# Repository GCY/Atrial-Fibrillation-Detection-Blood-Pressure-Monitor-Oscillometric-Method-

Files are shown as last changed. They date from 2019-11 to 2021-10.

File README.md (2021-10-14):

# Atrial-Fibrillation-Detection-Blood-Pressure-Monitor-Oscillometric-Method-
This project is electronic blood pressure monitor research platform with Oscillometric method, include SBP and DBP estimate algorithm, Atrial Fibrillation detection algorithm, calibration curve, GUI tool for fine-tune BP algorithm...etc, ofcourse, this is research use only.

<p align="center">
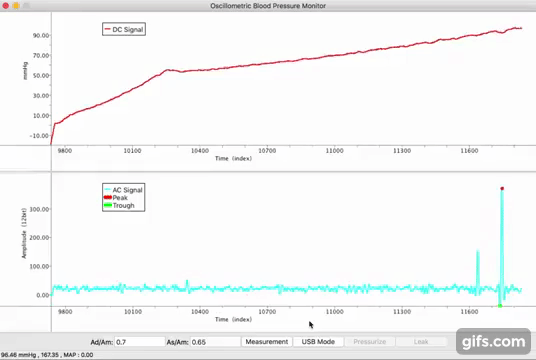
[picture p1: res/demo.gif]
  
</p>  

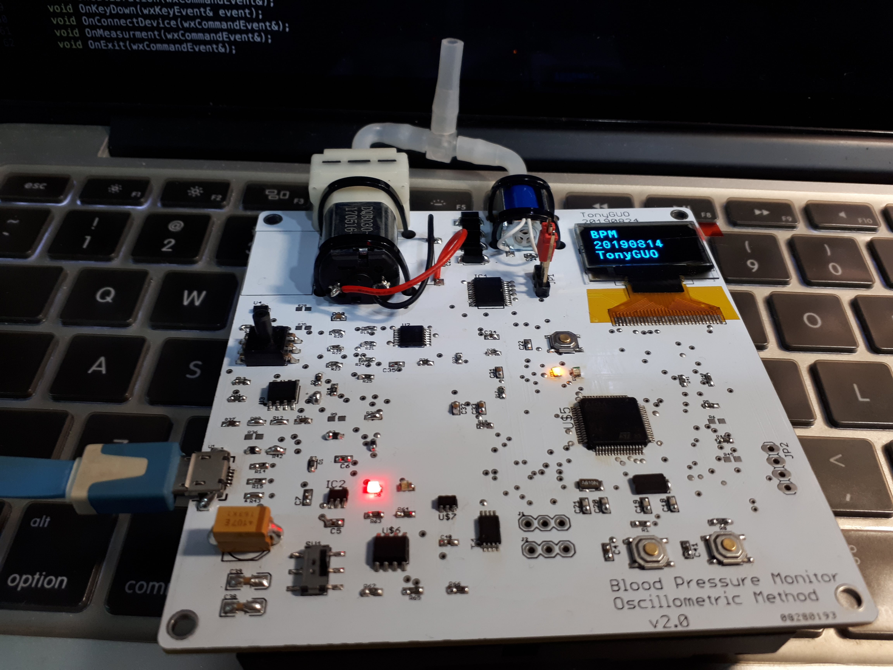
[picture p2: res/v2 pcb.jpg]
  

## Blood Pressure Measurement Oscillometric Method

The oscillometric method was first demonstrated in 1876 and involves the observation of oscillations in the sphygmomanometer cuff pressure which are caused by the oscillations of blood flow, It uses a sphygmomanometer cuff, like the auscultatory method, but with an electronic pressure sensor (transducer) to observe cuff pressure oscillations, electronics to automatically interpret them, and automatic inflation and deflation of the cuff. The pressure sensor should be calibrated periodically to maintain accuracy.

A new analysis of relevant anatomy, physiology and physics reveals the mechanisms underlying the production of cuff pressure oscillations as well as a way to extract systolic and diastolic pressures from the envelope of oscillations in any individual subject. Stiffness characteristics of the compressed artery segment can be extracted from the envelope shape to create an individualized mathematical model. The model is tested with a matrix of possible systolic and diastolic pressure values, and the minimum least squares difference between observed and predicted envelope functions indicates the best fit choices of systolic and diastolic pressure within the test matrix.

In practice the different methods do not give identical results; an algorithm and experimentally obtained coefficients are used to adjust the oscillometric results to give readings which match the auscultatory results as well as possible. Accurate extraction of systolic and diastolic pressures from the envelope of cuff pressure oscillations remains an open problem in biomedical engineering. Since many oscillometric devices have not been validated, caution must be given as most are not suitable in clinical and acute care settings.

via [wiki.](https://en.wikipedia.org/wiki/Blood_pressure_measurement)

## Features
- [x] Blood Pressure Measurment - Systolic, Diastolic, Mean
- [x] Atrial Fibrillation Detection - Irregular Pulse Peak , Irregular Heart Beats
- [x] GUI Toos - Algorithm Finetune
- [x] ADC Clibration to Mercury Manometer Pressure - Polynomial Curve Fit
- [x] RAW Data Record

## Hardware

Project create is Eagle PCB 8.1.0 .</br>

<strong>V2 version, D1(BAT20) should be replaced with zero ohm resistor.</strong></br>

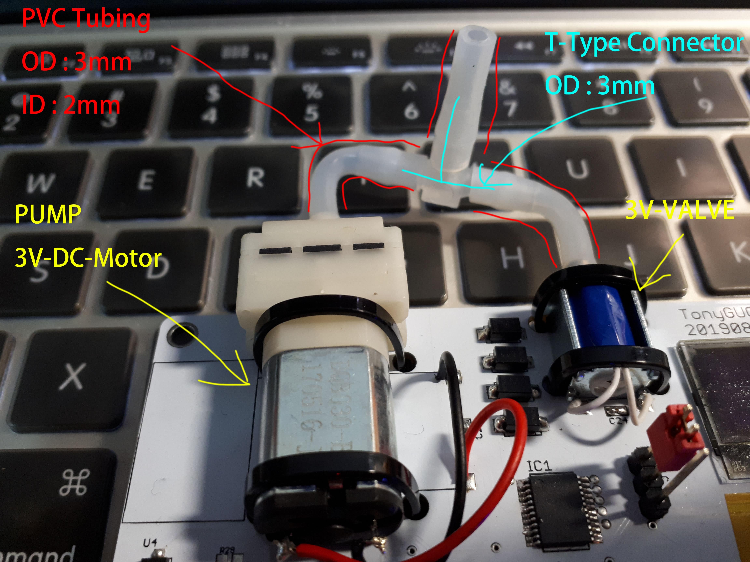
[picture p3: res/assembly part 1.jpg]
 

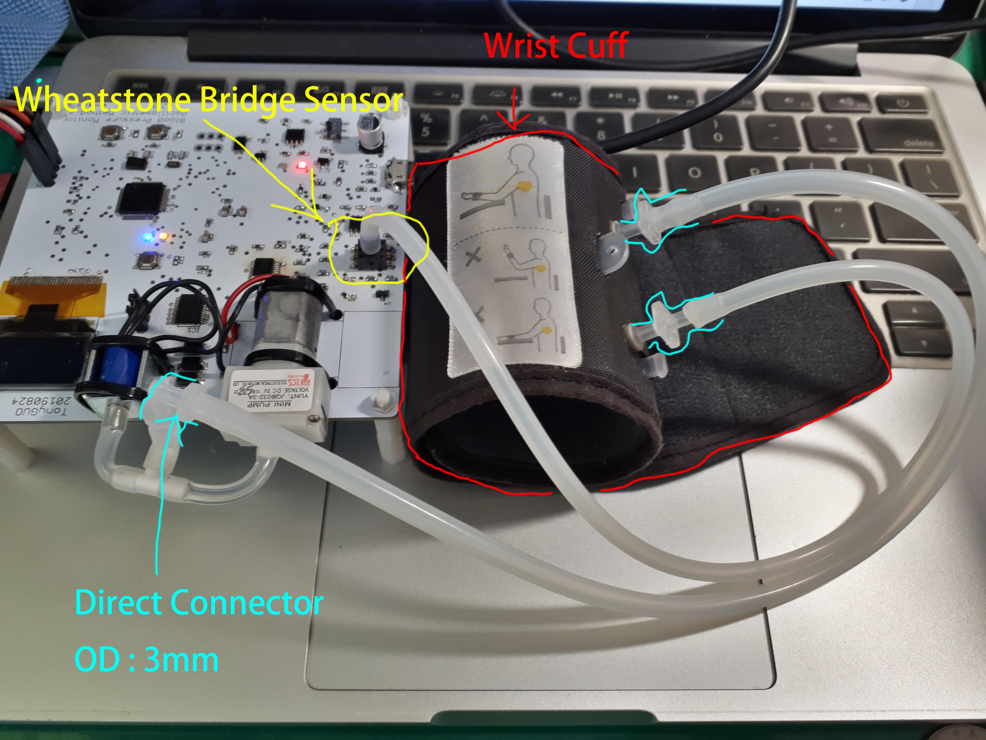
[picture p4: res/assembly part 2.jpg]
 

 

### Key Component List

- Electronics
  - TB6612FNG (for PUMP and VALVE PID control)
  - MPS-3117-006GC A2/A3(MEMS Wheatstone Bridge)
- Mechatronic
  - 3V DC Air Pump Motor(JQB032-3A or DQB030-A-3V)
  - 3V DC Electric Solenoid Valve(JQF1-3C1/DC3V Mini 10mm*15mm)
- Cuff and Tubing
  - 2mm*4mm Silicone Rubber Tubing x 2(20cm~30cm, for wrist cuff input and output)
  - 2mm*4mm Silicone Rubber Tubing x 3(5cm~10cm, for T Type connector)
  - 2mm*3mm T Type Plastic Barbed Connector
  - 2mm*3mm Straight Plastic Barbed Connector x 3
  - Wrist Air Cuff Input/Output(2 pinhole 2mm~3mm)
  
### Configure for Motor Electric Drives With Independent Power Supply - Battery2(U$19)
- J1, J2 pin1 connect to pin2 - battery2 charge
- J1, J2 pin2 connect to pin3 - motor drive with independent power supply
- JP1 pin1 connect to pin2 - motor drive with VCC
- JP1 pin2 connect to pin3 - motor drive with independent power supply

## Firmware

### Build and Burn The .elf
- 1.cd src/BPM
- 2.make
- 3.load main.elf

### Key Parameters

PWM_Freq is DC Motor PWM frequency.</br>
TIM_Prescaler = (168M/2)/1M = 84M</br>
TIM_Period = TIMER_PWM_MAX/PWM_Freq = 1000</br>

TIM = 84M / TIM_Prescaler = 1M</br>
TIM = 1M / TIM_ClockDivision = 1M</br>
1M / (TIM_Period + 1) = 1000Hz (1ms)</br>
<pre><code>
const uint16_t PWM_Freq = 1000;
</code></pre>

ARR = TIMER_PWM_MAX;</br>
CCR = 0 to TIMER_PWM_MAX = 0 to 100% PWM.</br>
In this case, PID PWM step 1 to 100 mapped to 100000 to 1000000.</br>
TIMER_PWM_33 and TIMER_PWM_40 is 33% and 40% PWM for calibration hand control.</br>
<pre><code>
const uint32_t PID_PWM_MIN = 1;
const uint32_t PID_PWM_MAX = 100;
const uint32_t TIMER_PWM_MIN = 100000;
const uint32_t TIMER_PWM_MAX; = 1000000;
const uint32_t TIMER_PWM_33 = 330000;
const uint32_t TIMER_PWM_40 = 400000;
</code></pre>

This is PID parameter, you need to redefine in ResetMeasurementParameter() function.</br>
<pre><code>
Kp = 2, Ki = 0.3, Kd = 0.001; // for JQB032-3A
</code></pre>

AC signal amplitude point of Systolic and Diastolic BP.</br>
<pre><code>
float as_am_value = 0.65f;
float ad_am_value = 0.7f;
</code></pre>

Polynomial curve fitting is generated from 『Calibration ADC-DC to Mercury Manometer Pressure』, you'll need to create 『curve.csv』and execute PC-GUI software main.app or BPM.exe in the same folder, it will output the『equation.txt』.</br>
e.g. degree = 2, equation.txt format is : (-1.0620516546)x^0+(0.1262915457)x^1+(-0.0000012119)x^2 </br>
<pre><code>
float a[3] = {-0.0000012119f,0.1262915457f,-1.0620516546f};
</code></pre>

If pulse_value_N / total_pulse_value_mean > IPP_Ratio, pulse_N is irregular pulse peak, and IPP ratio range 15%~25%.</br>
If IPP number / total_pulse_number > IHB_Ratio, this measurement is irregular heart beat.</br>
If two or more IHB of the three BP measurements, AF detected.<br>
<pre><code>
const float IPP_Ratio = 0.2f;
const float IHB_Ratio = 0.2f;
</code></pre>

### Operation Flowchart
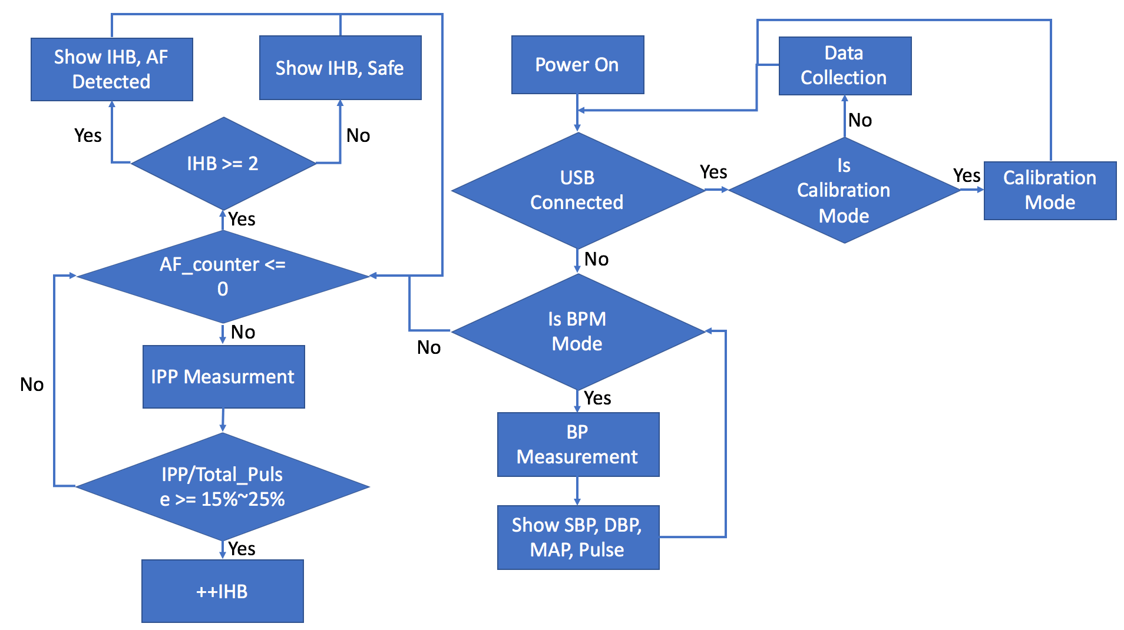
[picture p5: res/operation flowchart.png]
  

### DC/AC Signal Process Flowchart
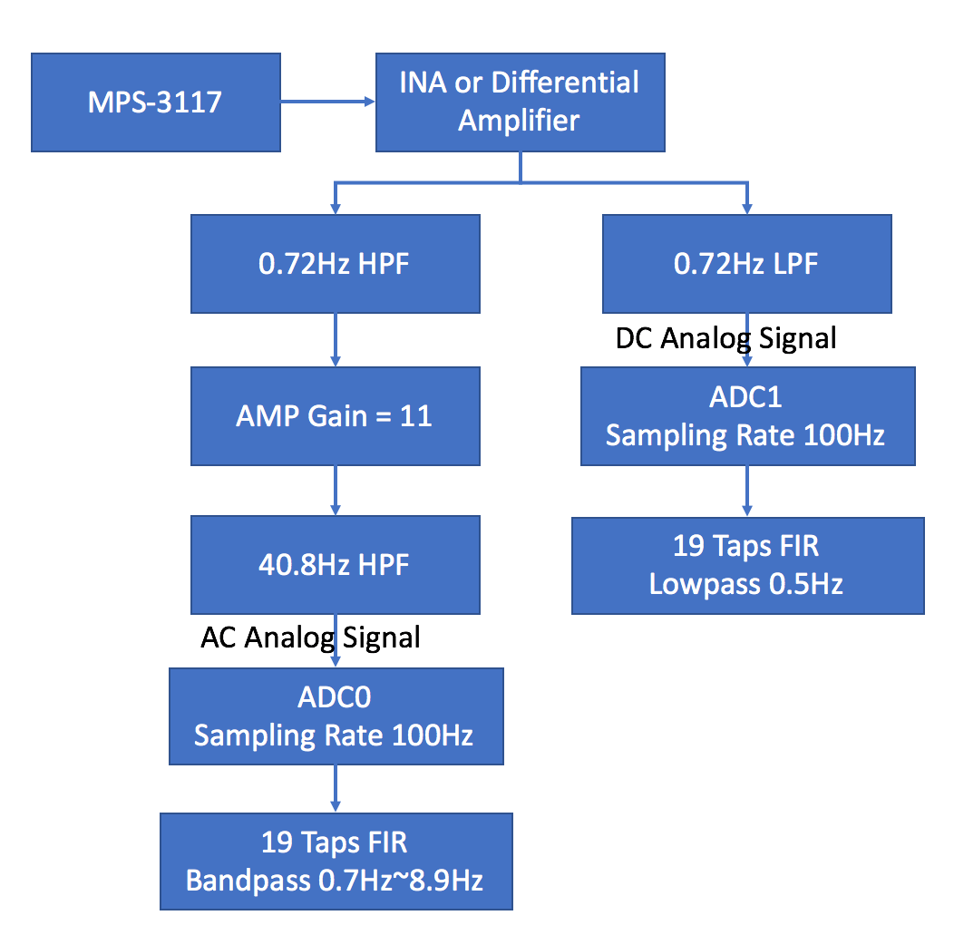
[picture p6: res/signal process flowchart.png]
  

### Measurment Flowchart
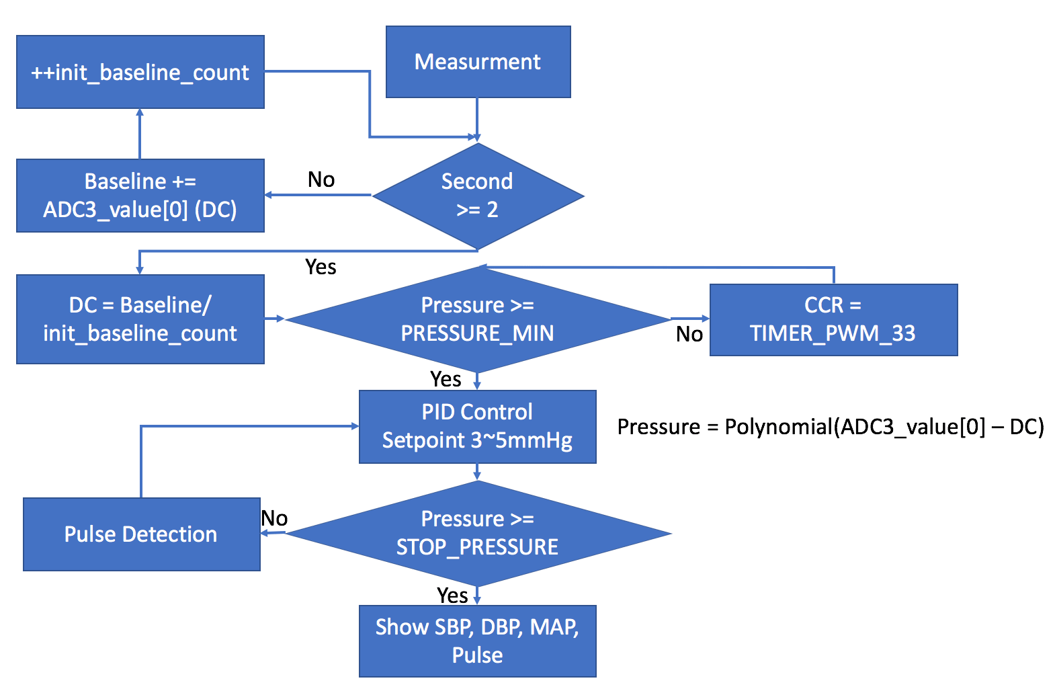
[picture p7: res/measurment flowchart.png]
 

### BPM Mode Demo
Audi R8 (https://youtu.be/4AQXaJOquz4)

## Software

### AFib-BPM GUI Demo
Audi R8 (https://youtu.be/8z78SInvyog)

### Build
- Win10
  - 1.Open BPM.sln
  - 2.Rebuild
- Mac High Sierra
  - 1.make
  
### Dependence
- Win10
  - wxWidgets 3.1.2
  - VS2017 - MSVC 10.0.17763-SDK
- Mac High Sierra
  - wxWidgets 3.x
  - g++

### Parameters Setup
When burning the firmware for the first time, you must set the PID control and blood pressure algorithm parameters. After the PC-Host and VCP are successfully connected, select the Tuning menu to adjust the parameters.</br>

  
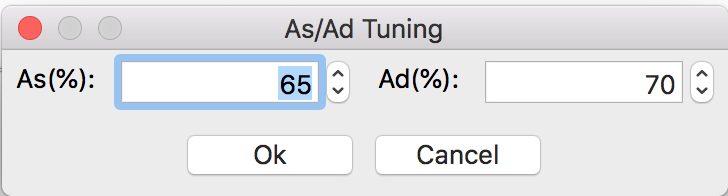
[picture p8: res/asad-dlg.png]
  

Display the parameters that have been set. If the parameters are unset, the value is "0xFFFFFFFF" in sector11 of flash. The PID parameters shown in the figure need to be divided by hundred. (for example, P = 290, in firmware, P is 2.9 .)</br>

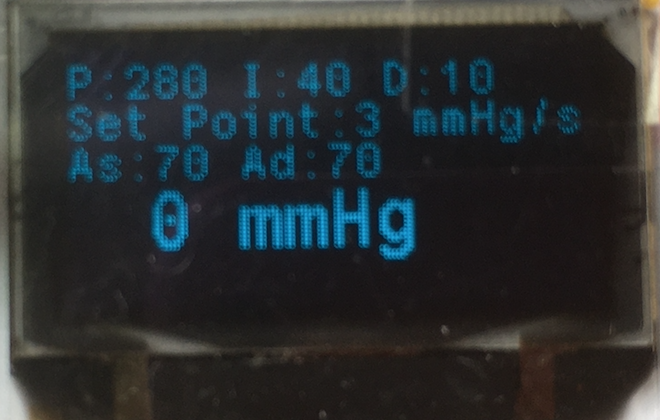
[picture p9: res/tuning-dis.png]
  

### Mac High Sierra GUI
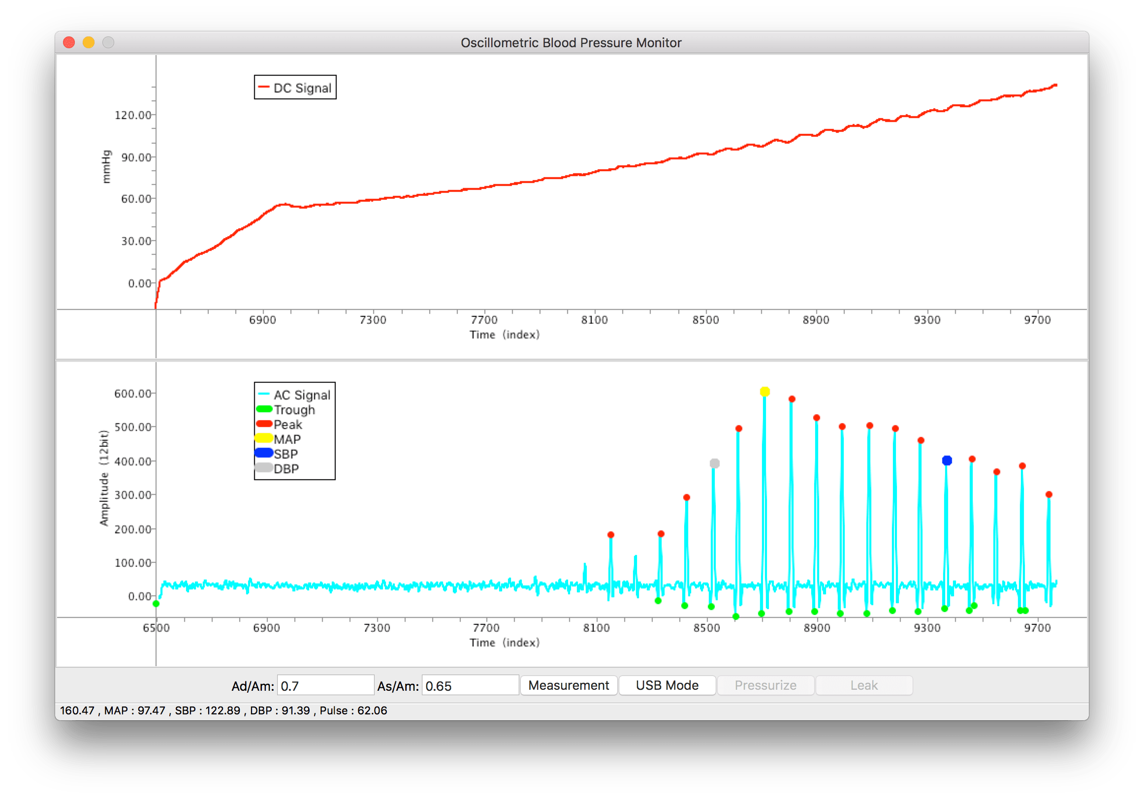
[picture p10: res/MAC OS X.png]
  

### Win10 GUI
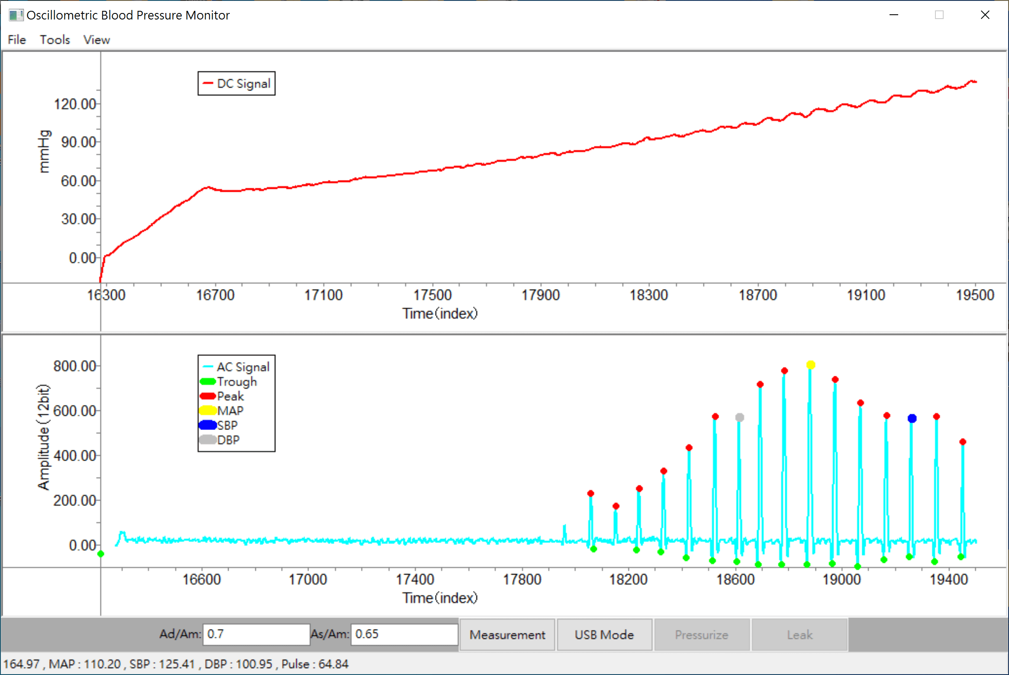
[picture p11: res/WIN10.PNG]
  

### Operation Manual
- Menu Tools -> VCP is connect to device.
- "Ad/Am" and "As/Am" text box is Diastolic and Systolic BP Point of AC signal amplitude.
- "Measurment" button is BP measurment after VCP connected.
- "USB Mode" button is switch from "USB Mode"(Measurment) to "Calibration Mode", and vice versa.
- "Pressurize" and "Leak" button for control mercury manometer high and low in calibration mode.

## Oscillometric Method
The two chart below show AC signal types, all of types are correct.

### Type1 AC Signal
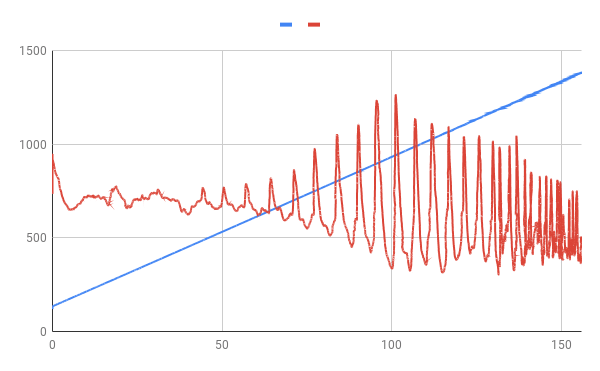
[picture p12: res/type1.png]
  

### Type2 AC Signal
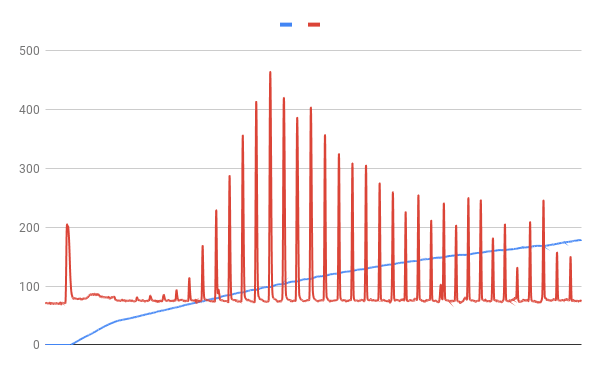
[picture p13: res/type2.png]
  

## Calibration ADC-DC to Mercury Manometer Pressure

Pressure calibration reference is Mercury Manometer(Sphygmomanometer) or Aneroid Sphygmomanometer, you can buy products from Yuwell, Welch Allyn...etc </br>

### PC-GUI Software Control Steps
- 1.Connecting device and PC-GUI software.
- 2.Click USB Mode button switch to Calibration Mode, after this, OLED display show you ADC0 value per-second.
- 3.Control Mercury Manometer high and low with Presurize and Leak button.
- 4.Record Mercury Manometer pressure point and OLED ADC0 value to 『curve.csv』file, at least 10-points and pressure range 0~250mmHg. 
- 5.checking curve.csv is located in the same folder as the PC-GUI software.
- 6.Close PC-GUI software than reopen it, it will generate the『equation.txt』.
- 7.copy equation and replace firmware parameter 『float a[3]』 in main.c.

Column A is ADC0-value, B is Mercury Manometer mmHg pressure.</br>
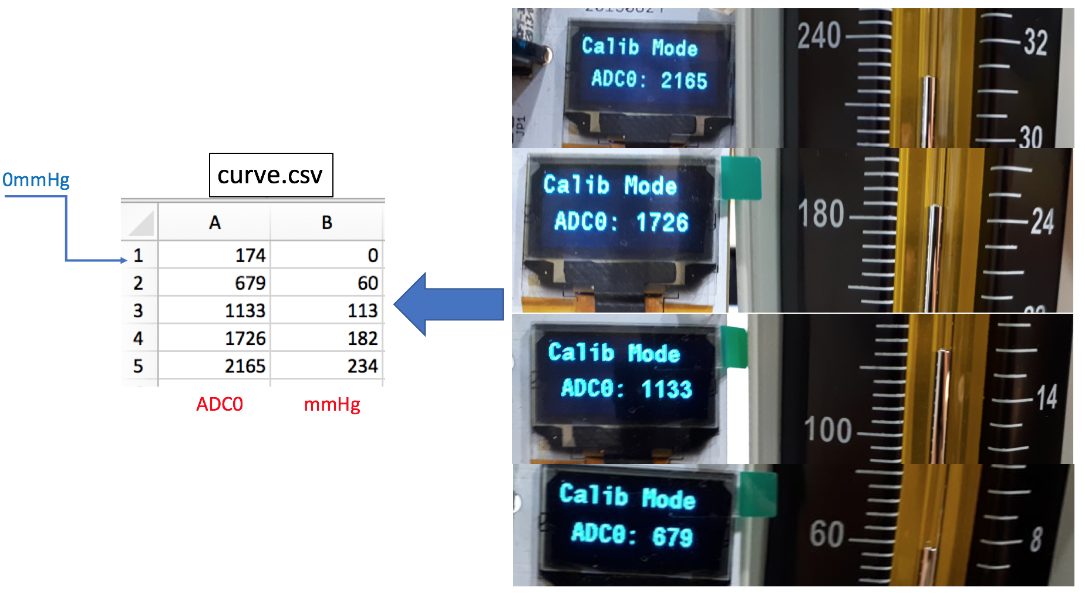
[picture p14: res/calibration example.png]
  

## Atrial Fibrillation In Oscillometric Method Detect Algorithm

Below are a few real world cases of the AFib(for example PCV, PAC), envelope wave lost some peaks.</br>

### Premature Atrial Contractions

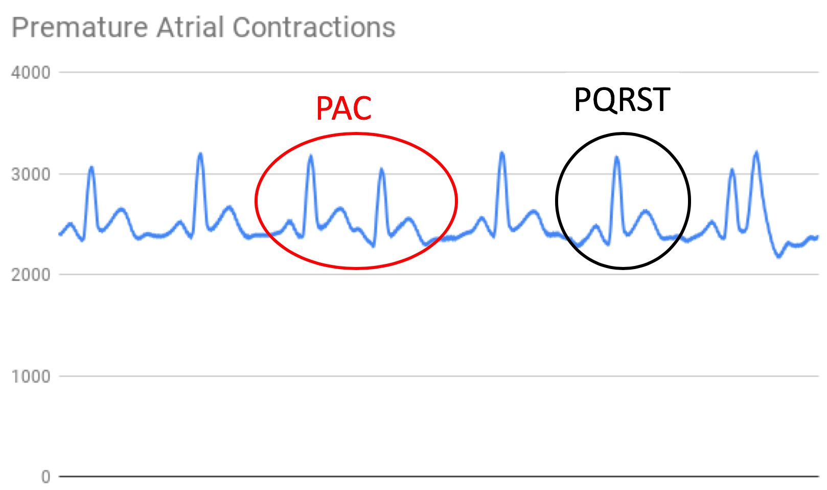
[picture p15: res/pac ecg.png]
  

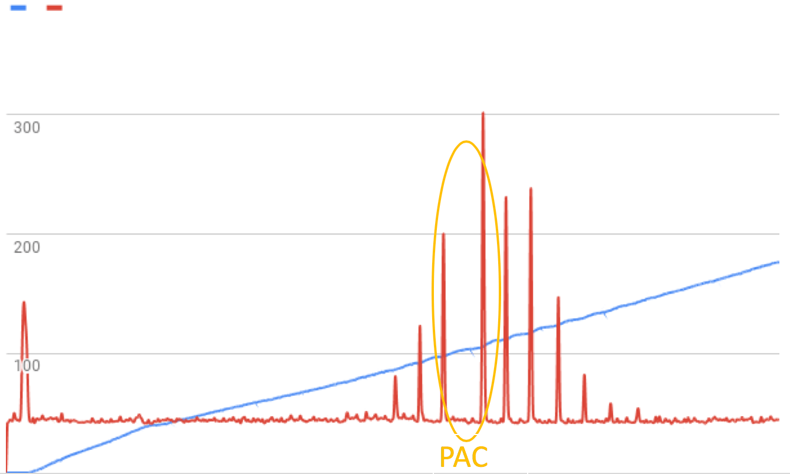
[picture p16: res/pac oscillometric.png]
  

### Premature Ventricular Contractions

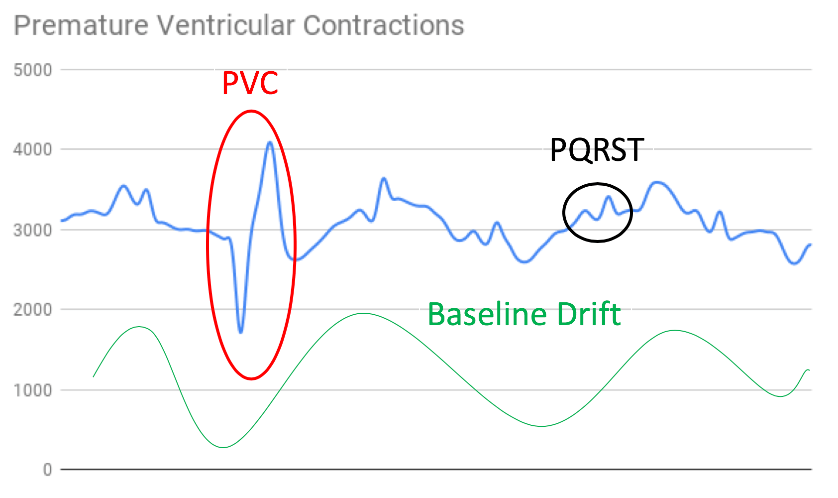
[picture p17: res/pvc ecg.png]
  

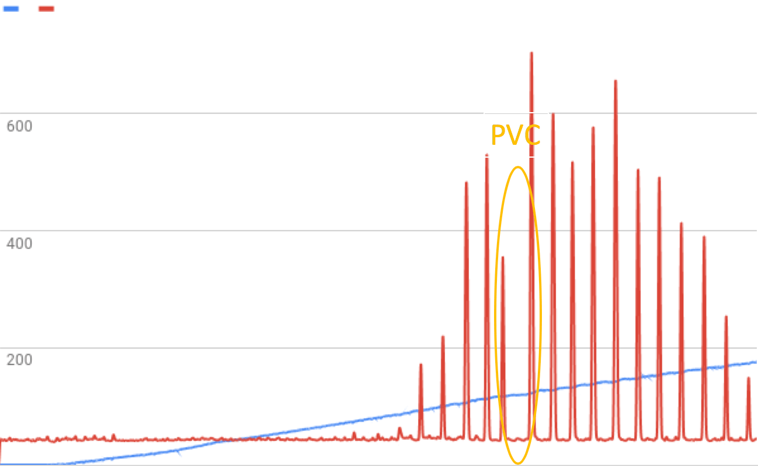
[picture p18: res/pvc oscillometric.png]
  

## Reference
- Kabutoya, T., Imai, Y., Hoshide, S., & Kario, K. (2017). Diagnostic accuracy of a new algorithm to detect atrial fibrillation in a home blood pressure monitor. The Journal of Clinical Hypertension, 19(11), 1143-1147.

- Ogedegbe, G., & Pickering, T. (2010). Principles and techniques of blood pressure measurement. Cardiology clinics, 28(4), 571-586.

- Babbs, C. F. (2012). Oscillometric measurement of systolic and diastolic blood pressures validated in a physiologic mathematical model. Biomedical engineering online, 11(1), 56.

- Geddes, L. A., Voelz, M., Combs, C., Reiner, D., & Babbs, C. F. (1982). Characterization of the oscillometric method for measuring indirect blood pressure. Annals of biomedical engineering, 10(6), 271-280.

- C++ Program for Polynomial Fit (Least Squares) : https://www.bragitoff.com/2015/09/c-program-for-polynomial-fit-least-squares/

LICENSE
-------

MIT License

Copyright (c) 2019 Tony Guo

Permission is hereby granted, free of charge, to any person obtaining a copy
of this software and associated documentation files (the "Software"), to deal
in the Software without restriction, including without limitation the rights
to use, copy, modify, merge, publish, distribute, sublicense, and/or sell
copies of the Software, and to permit persons to whom the Software is
furnished to do so, subject to the following conditions:

The above copyright notice and this permission notice shall be included in all
copies or substantial portions of the Software.

THE SOFTWARE IS PROVIDED "AS IS", WITHOUT WARRANTY OF ANY KIND, EXPRESS OR
IMPLIED, INCLUDING BUT NOT LIMITED TO THE WARRANTIES OF MERCHANTABILITY,
FITNESS FOR A PARTICULAR PURPOSE AND NONINFRINGEMENT. IN NO EVENT SHALL THE
AUTHORS OR COPYRIGHT HOLDERS BE LIABLE FOR ANY CLAIM, DAMAGES OR OTHER
LIABILITY, WHETHER IN AN ACTION OF CONTRACT, TORT OR OTHERWISE, ARISING FROM,
OUT OF OR IN CONNECTION WITH THE SOFTWARE OR THE USE OR OTHER DEALINGS IN THE
SOFTWARE.

OSHW Certification
-------

https://certification.oshwa.org/tw000002.html

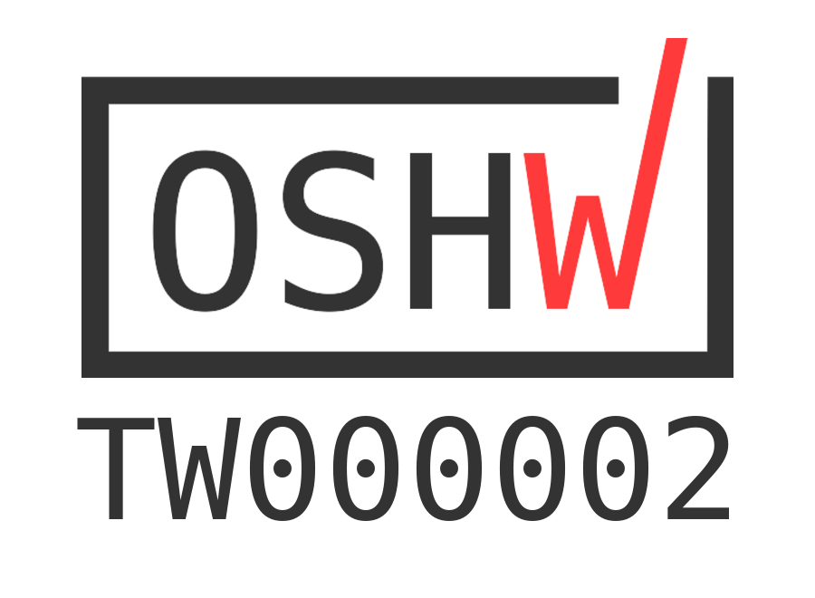
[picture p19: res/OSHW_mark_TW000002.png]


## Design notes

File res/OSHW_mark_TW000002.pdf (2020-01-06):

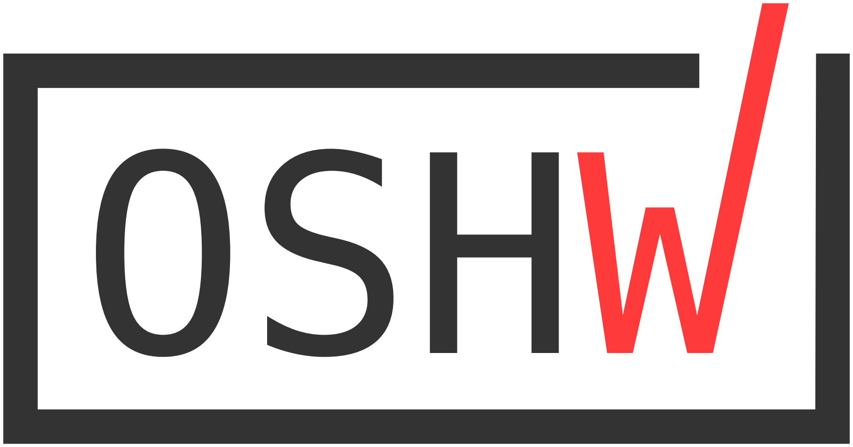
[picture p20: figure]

TW000002

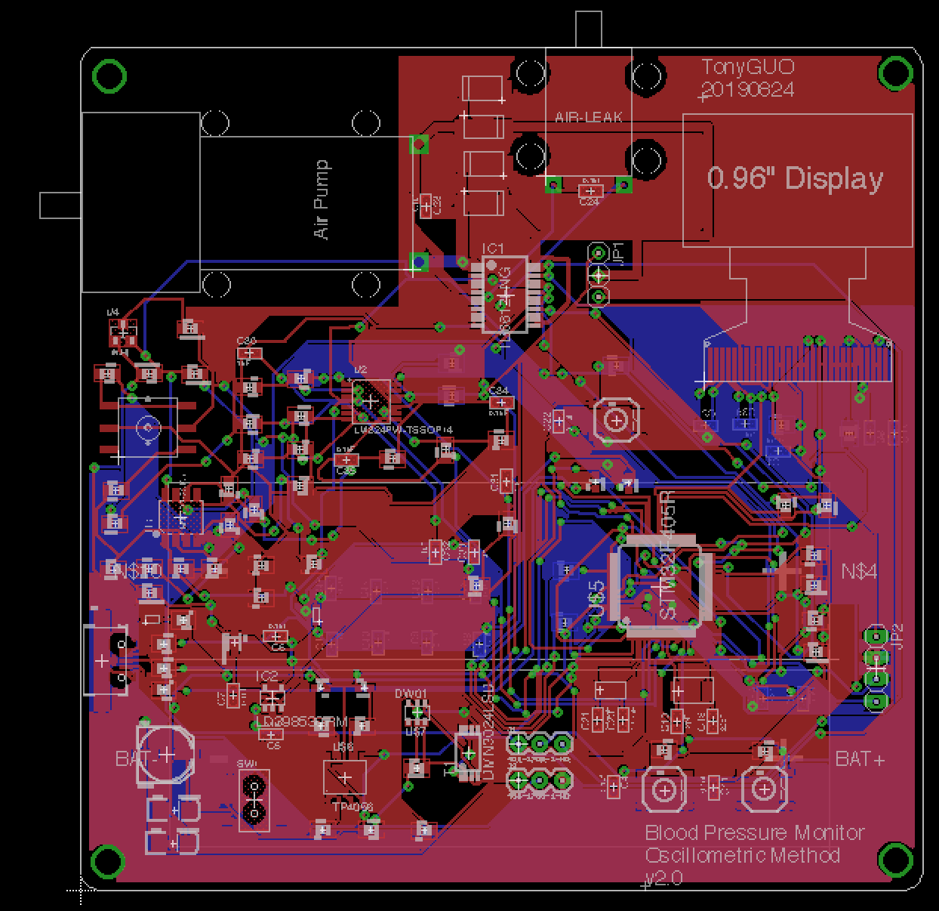
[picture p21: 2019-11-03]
hardware/Oscillometric Method Blood Pressure Monitor v2/pcb layout.png

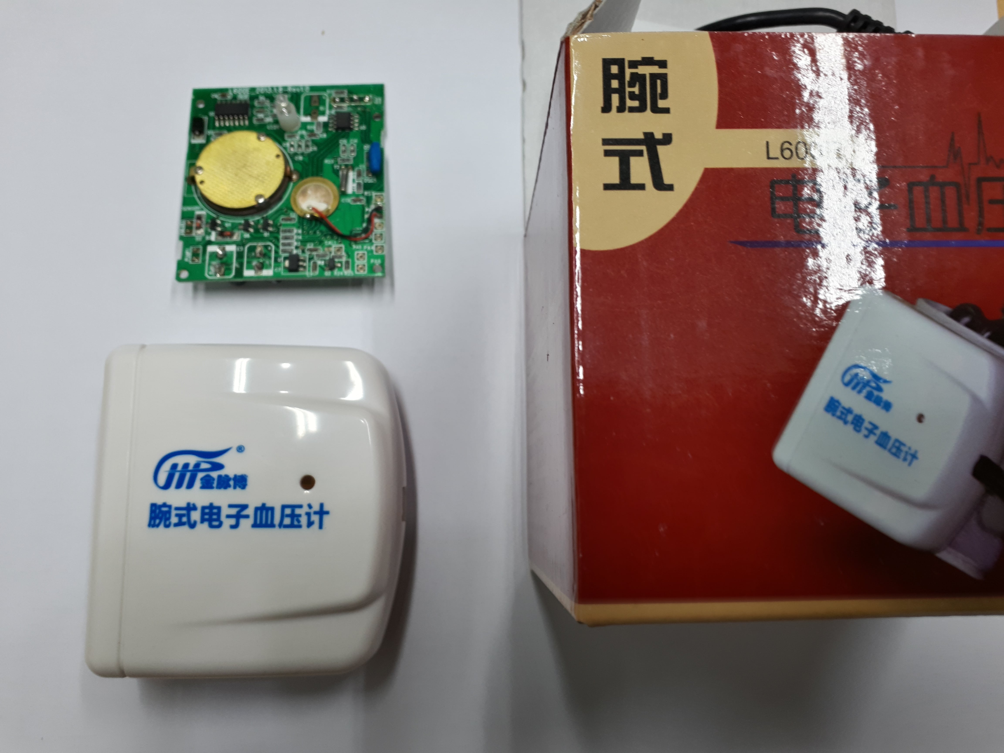
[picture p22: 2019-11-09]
res/pump&valve source XD .jpg

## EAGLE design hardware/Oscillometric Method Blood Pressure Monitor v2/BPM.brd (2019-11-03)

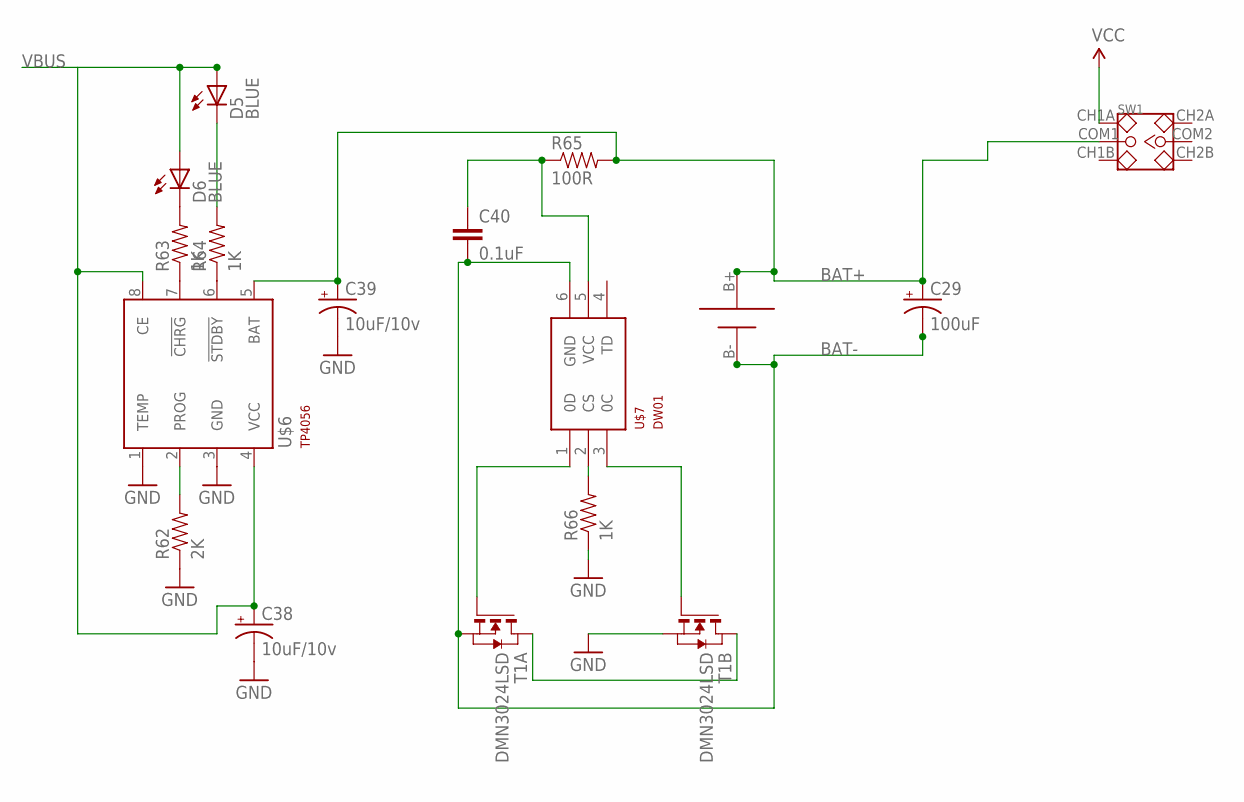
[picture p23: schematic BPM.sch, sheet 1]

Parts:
C29: 100uF; NIPPON_F80
C38, C39: 10uF/10v; EIA3216-KIT
C40: 0.1uF; 0603-CAP
D5, D6: BLUE; LED-0603
R62: 2K; 0603-RES
R63, R64, R66: 1K; 0603-RES
R65: 100R; 0603-RES
SW1: SMD-TOGGLE-SWITCH-2CH(2X3P-7X3.5MM); SW6-2.54-SMD-7.0X3.5X1.5MM
T1: DMN3024LSD; TSSOP-8
U$4: 18650SMD
U$6: TP4056; SOT23-8
U$7: DW01; SOT23-6

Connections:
BAT+: C29.+, C39.A (+), R65.2, SW1.COM1, U$4.B+, U$6.5 (BAT); also elsewhere on the board
BAT-: C29.-, C40.2, T1.2 (S), T1.3 (S), U$4.B-, U$7.6 (GND); also elsewhere on the board
GND: C38.C (-), C39.C (-), R62.1, R66.1, T1.6 (S), T1.7 (S), U$6.1 (TEMP), U$6.3 (GND); also elsewhere on the board
unnamed: R62.2, U$6.2 (PROG)
unnamed: R63.1, U$6.7 (!CHRG)
unnamed: R64.1, U$6.6 (!STDBY)
unnamed: D6.C, R63.2
unnamed: D5.C, R64.2
unnamed: C40.1, R65.1, U$7.5 (VCC)
unnamed: T1.4 (G), U$7.1 (0D)
unnamed: R66.2, U$7.2 (CS)
unnamed: T1.1 (D), T1.8 (D)
unnamed: T1.5 (G), U$7.3 (0C)
VBUS: C38.A (+), D5.A, D6.A, U$6.4 (VCC), U$6.8 (CE); also elsewhere on the board
VCC: SW1.CH1A; also elsewhere on the board

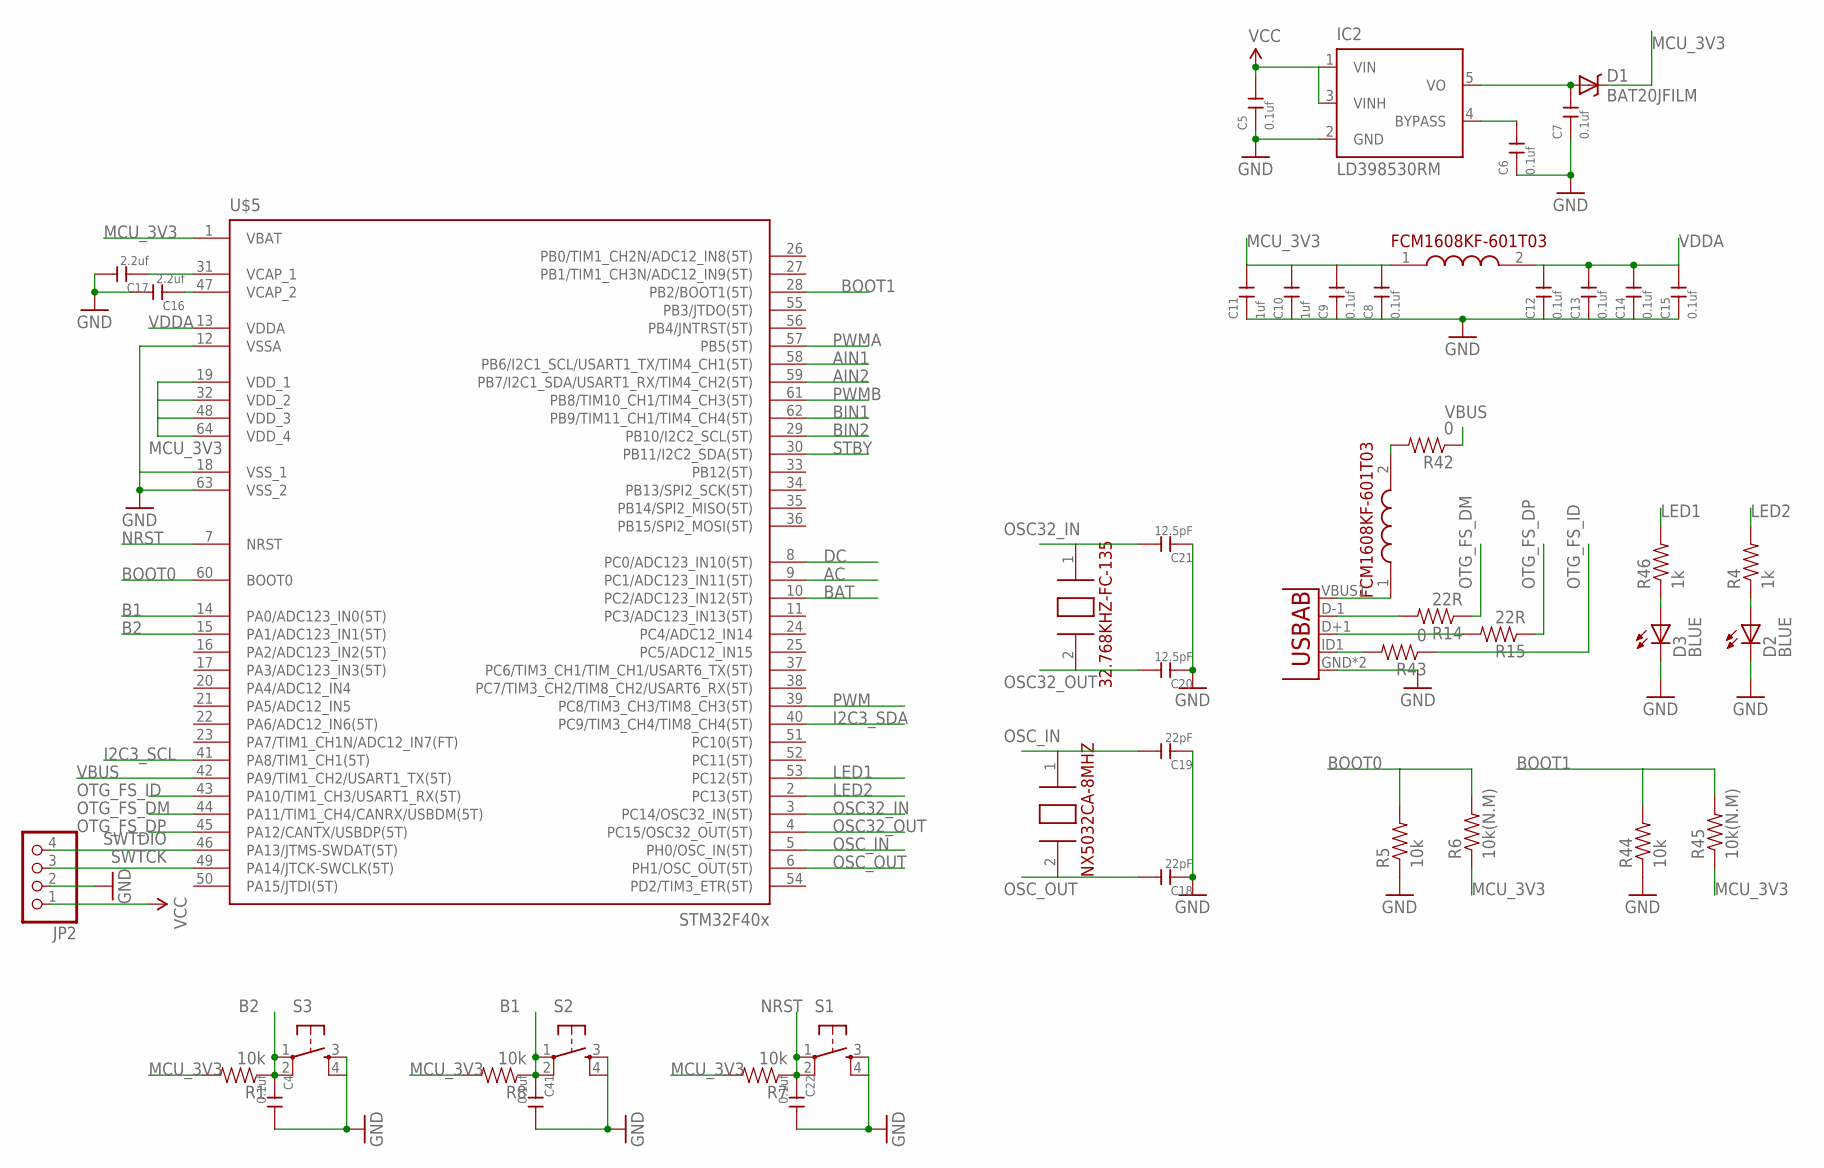
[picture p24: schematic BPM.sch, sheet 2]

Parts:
C4, C5, C6, C7, C8, C9, C12, C13, C14, C15, C22, C41: 0.1uf; C0603
C10, C11: 1uf; C0603
C16, C17: 2.2uf; C0603
C18, C19: 22pF; C0603
C20, C21: 12.5pF; C0603
D1: BAT20JFILM; SOD-323
D2, D3: BLUE; LED-0603
IC2: LD398530RM; SOT23-5L
JP2: PINHD-1X4; 1X04
R1, R5, R7, R8, R44: 10k; 0603
R4, R46: 1k; 0603
R6, R45: 10k(N.M); 0603
R14, R15: 22R; 0603-RES
R42, R43: 0; 0603-RES
S1, S2, S3: TAC_SWITCHSMD; TACTILE_SWITCH_SMD
U1: USB""; USB-MICRO-SMD
U$5: STM32F405R; TQFP64
U$8: 32.768KHZ-FC-135
U$9: NX5032CA-8MHZ
U$10, U$15: FCM1608KF-601T03

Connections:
AC: U$5.9 (PC1/ADC123_IN11(5T)); also elsewhere on the board
AIN1: U$5.58 (PB6/I2C1_SCL/USART1_TX/TIM4_CH1(5T)); also elsewhere on the board
AIN2: U$5.59 (PB7/I2C1_SDA/USART1_RX/TIM4_CH2(5T)); also elsewhere on the board
B1: C41.1, R8.1, S2.1, S2.2, U$5.14 (PA0/ADC123_IN0(5T))
B2: C4.1, R1.1, S3.1, S3.2, U$5.15 (PA1/ADC123_IN1(5T))
BAT: U$5.10 (PC2/ADC123_IN12(5T)); also elsewhere on the board
BIN1: U$5.62 (PB9/TIM11_CH1/TIM4_CH4(5T)); also elsewhere on the board
BIN2: U$5.29 (PB10/I2C2_SCL(5T)); also elsewhere on the board
BOOT0: R5.2, R6.2, U$5.60 (BOOT0)
BOOT1: R44.2, R45.2, U$5.28 (PB2/BOOT1(5T))
DC: U$5.8 (PC0/ADC123_IN10(5T)); also elsewhere on the board
GND: C4.2, C5.1, C6.1, C7.1, C8.1, C9.1, C10.1, C11.1, C12.1, C13.1, C14.1, C15.1, C16.2, C17.2, C18.1, C19.1, C20.1, C21.1, C22.2, C41.2, D2.C, D3.C, IC2.2 (GND), JP2.2, R5.1, R44.1, S1.3, S1.4, S2.3, S2.4, S3.3, S3.4, U1.GND, U1.GND1 (GND), U$5.12 (VSSA), U$5.18 (VSS_1), U$5.63 (VSS_2); also elsewhere on the board
I2C3_SCL: U$5.41 (PA8/TIM1_CH1(5T)); also elsewhere on the board
I2C3_SDA: U$5.40 (PC9/TIM3_CH4/TIM8_CH4(5T)); also elsewhere on the board
LED1: R46.2, U$5.53 (PC12(5T))
LED2: R4.2, U$5.2 (PC13(5T))
MCU_3V3: C8.2, C9.2, C10.2, C11.2, D1.1 (C), R1.2, R6.1, R7.2, R8.2, R45.1, U$5.1 (VBAT), U$5.19 (VDD_1), U$5.32 (VDD_2), U$5.48 (VDD_3), U$5.64 (VDD_4), U$10.1 (1.IN); also elsewhere on the board
unnamed: D2.A, R4.1
unnamed: C17.1, U$5.31 (VCAP_1)
unnamed: C16.1, U$5.47 (VCAP_2)
unnamed: C6.2, IC2.4 (BYPASS)
unnamed: C7.2, D1.2 (A), IC2.5 (VO)
unnamed: R14.2, U1.D-1 (D-)
unnamed: R15.2, U1.D+1 (D+)
unnamed: R43.2, U1.ID1 (USBID)
unnamed: U1.VBUS1 (VBUS), U$15.1 (1.IN)
unnamed: R42.2, U$15.2 (2.OUT)
unnamed: D3.A, R46.1
NRST: C22.1, R7.1, S1.1, S1.2, U$5.7 (NRST)
OSC32_IN: C21.2, U$5.3 (PC14/OSC32_IN(5T)), U$8.1 (1.XIN)
OSC32_OUT: C20.2, U$5.4 (PC15/OSC32_OUT(5T)), U$8.2 (2.XIN)
OSC_IN: C19.2, U$5.5 (PH0/OSC_IN(5T)), U$9.1 (1.XIN)
OSC_OUT: C18.2, U$5.6 (PH1/OSC_OUT(5T)), U$9.2 (2.XOUT)
OTG_FS_DM: R14.1, U$5.44 (PA11/TIM1_CH4/CANRX/USBDM(5T))
OTG_FS_DP: R15.1, U$5.45 (PA12/CANTX/USBDP(5T))
OTG_FS_ID: R43.1, U$5.43 (PA10/TIM1_CH3/USART1_RX(5T))
PWM: U$5.39 (PC8/TIM3_CH3/TIM8_CH3(5T)); also elsewhere on the board
PWMA: U$5.57 (PB5(5T)); also elsewhere on the board
PWMB: U$5.61 (PB8/TIM10_CH1/TIM4_CH3(5T)); also elsewhere on the board
STBY: U$5.30 (PB11/I2C2_SDA(5T)); also elsewhere on the board
SWTCK: JP2.3, U$5.49 (PA14/JTCK-SWCLK(5T))
SWTDIO: JP2.4, U$5.46 (PA13/JTMS-SWDAT(5T))
VBUS: R42.1, U$5.42 (PA9/TIM1_CH2/USART1_TX(5T)); also elsewhere on the board
VCC: C5.2, IC2.1 (VIN), IC2.3 (VINH), JP2.1; also elsewhere on the board
VDDA: C12.2, C13.2, C14.2, C15.2, U$5.13 (VDDA), U$10.2 (2.OUT)

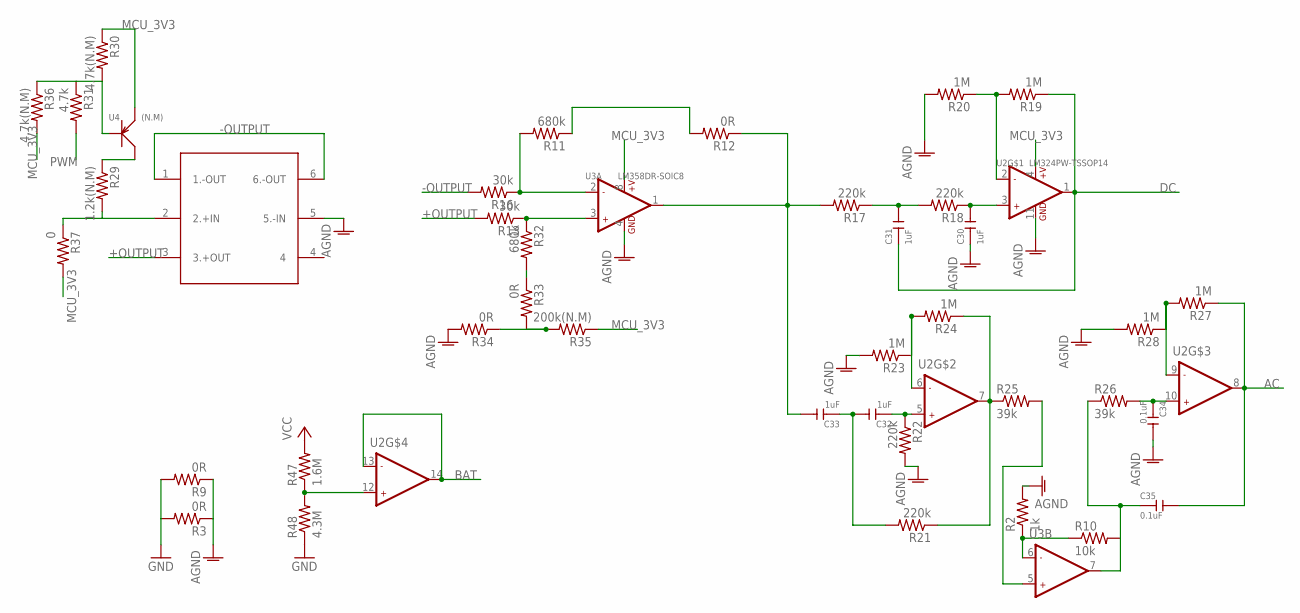
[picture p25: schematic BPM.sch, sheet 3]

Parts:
C30, C31, C32, C33: 1uF; C0603
C34, C35: 0.1uF; C0603
R2: 1k; 0603
R3, R9, R12, R33, R34: 0R; 0603
R10: 10k; 0603
R11, R32: 680k; 0603
R13, R16: 30k; 0603
R17, R18, R21, R22: 220k; 0603
R19, R20, R23, R24, R27, R28: 1M; 0603
R25, R26: 39k; 0603
R29: 1.2k(N.M); 0603
R30, R36: 4.7k(N.M); 0603
R31: 4.7k; 0603
R35: 200k(N.M); 0603
R37: 0; 0603
R47: 1.6M; 0603
R48: 4.3M; 0603
U2: LM324PW-TSSOP14; TSSOP14-0.65-5X4.4MM
U3: LM358DR-SOIC8; SOIC8-1.27-5X4MM
U4: (N.M); SOT-23
U$1: MPS-3117-006G

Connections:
+OUTPUT: R13.2, U$1.3 (3.+OUT)
-OUTPUT: R16.2, U$1.1 (1.-OUT), U$1.6 (6.-OUT)
AC: C35.2, R27.1, U2.8 (OUT2); also elsewhere on the board
AGND: C30.1, C34.2, R2.2, R3.1, R9.1, R20.2, R22.2, R23.2, R28.2, R34.2, U2.11 (GND), U3.4 (GND), U$1.5 (5.-IN)
BAT: U2.13 (-IN2), U2.14 (OUT2); also elsewhere on the board
DC: C31.1, R19.1, U2.1 (OUT1); also elsewhere on the board
GND: R3.2, R9.2, R48.1; also elsewhere on the board
MCU_3V3: R30.1, R35.1, R36.2, R37.2, U2.4 (+V), U3.8 (+V), U4.2 (E); also elsewhere on the board
unnamed: C35.1, R10.2, R26.1, U3.7 (OUT2)
unnamed: R25.2, U3.5 (+IN2)
unnamed: R47.1, R48.2, U2.12 (+IN2)
unnamed: R2.1, R10.1, U3.6 (-IN2)
unnamed: R11.1, R12.2
unnamed: R11.2, R16.1, U3.2 (-IN1)
unnamed: C33.2, R12.1, R17.2, U3.1 (OUT1)
unnamed: R13.1, R32.1, U3.3 (+IN1)
unnamed: R29.2, R37.1, U$1.2 (2.+IN)
unnamed: C31.2, R17.1, R18.2
unnamed: C30.2, R18.1, U2.3 (+IN1)
unnamed: C32.1, R22.1, U2.5 (+IN2)
unnamed: R19.2, R20.1, U2.2 (-IN1)
unnamed: C32.2, C33.1, R21.2
unnamed: R21.1, R24.1, R25.1, U2.7 (OUT2)
unnamed: R23.1, R24.2, U2.6 (-IN2)
unnamed: R29.1, U4.3 (C)
unnamed: C34.1, R26.2, U2.10 (+IN2)
unnamed: R32.2, R33.1
unnamed: R27.2, R28.1, U2.9 (-IN2)
unnamed: R30.2, R31.1, R36.1, U4.1 (B)
unnamed: R33.2, R34.1, R35.2
PWM: R31.2; also elsewhere on the board
VCC: R47.2; also elsewhere on the board

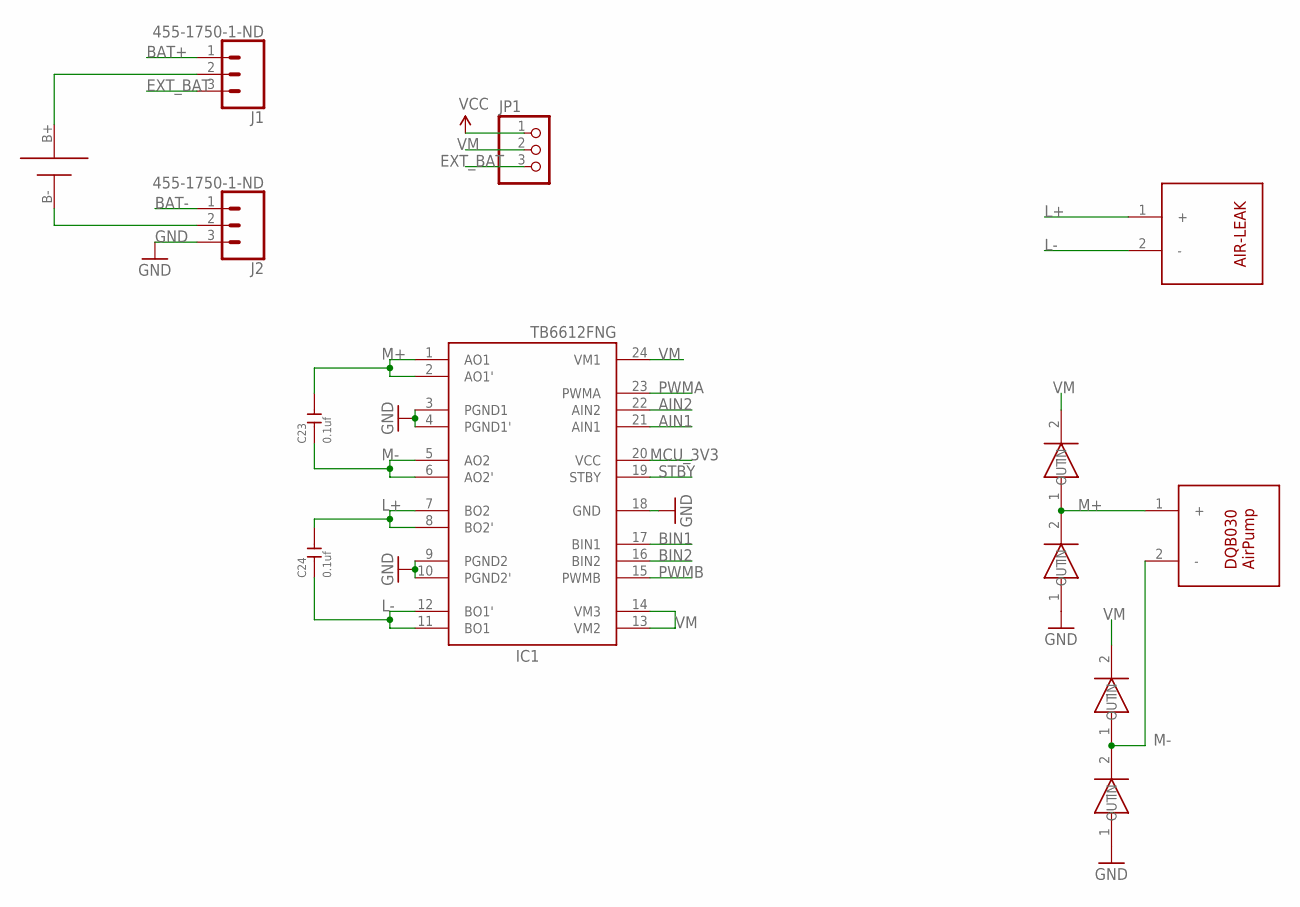
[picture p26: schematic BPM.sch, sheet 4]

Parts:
C23, C24: 0.1uf; C0603
IC1: TB6612FNG; SSOP24
J1, J2: 455-1750-1-ND; 1X03
JP1: PINHD-1X3; 1X03
U$11: AIR-LEAK
U$12: DQB030-AIRPUMP
U$13, U$14, U$16, U$17: SMA-SS34
U$19: 18650SMD

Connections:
AIN1: IC1.21 (AIN1); also elsewhere on the board
AIN2: IC1.22 (AIN2); also elsewhere on the board
BAT+: J1.1; also elsewhere on the board
BAT-: J2.1; also elsewhere on the board
BIN1: IC1.17 (BIN1); also elsewhere on the board
BIN2: IC1.16 (BIN2); also elsewhere on the board
EXT_BAT: J1.3, JP1.3
GND: IC1.3 (PGND1), IC1.4 (PGND1'), IC1.9 (PGND2), IC1.10 (PGND2'), IC1.18 (GND), J2.3, U$14.1 (IN), U$17.1 (IN); also elsewhere on the board
L+: C24.2, IC1.7 (BO2), IC1.8 (BO2'), U$11.1 (+)
L-: C24.1, IC1.11 (BO1), IC1.12 (BO1'), U$11.2 (-)
M+: C23.2, IC1.1 (AO1), IC1.2 (AO1'), U$12.1 (+), U$13.1 (IN), U$14.2 (OUT)
M-: C23.1, IC1.5 (AO2), IC1.6 (AO2'), U$12.2 (-), U$16.1 (IN), U$17.2 (OUT)
MCU_3V3: IC1.20 (VCC); also elsewhere on the board
unnamed: J1.2, U$19.B+
unnamed: J2.2, U$19.B-
PWMA: IC1.23 (PWMA); also elsewhere on the board
PWMB: IC1.15 (PWMB); also elsewhere on the board
STBY: IC1.19 (STBY); also elsewhere on the board
VCC: JP1.1; also elsewhere on the board
VM: IC1.13 (VM2), IC1.14 (VM3), IC1.24 (VM1), JP1.2, U$13.2 (OUT), U$16.2 (OUT)

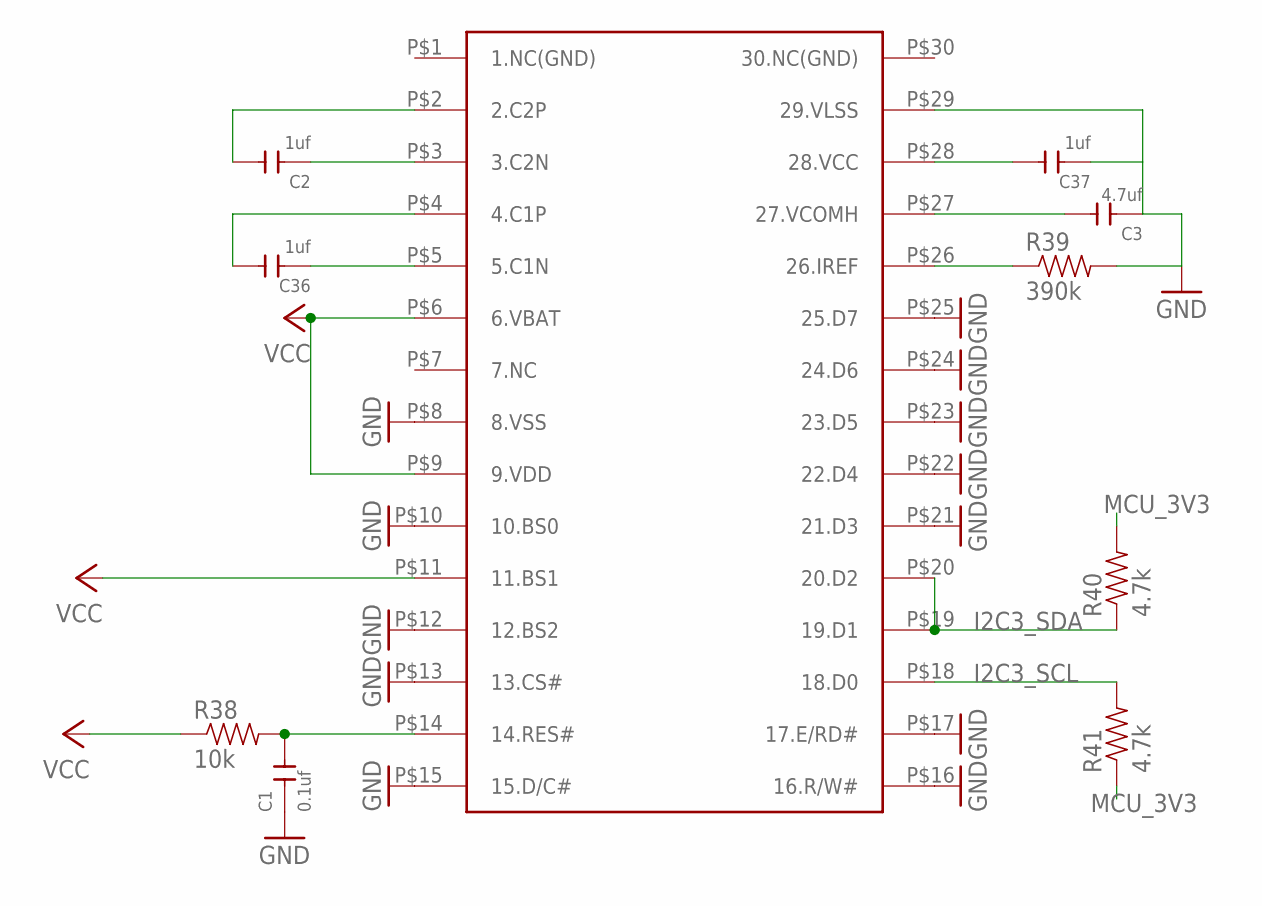
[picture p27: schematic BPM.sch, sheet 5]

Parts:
C1: 0.1uf; C0603
C2, C36, C37: 1uf; C0603
C3: 4.7uf; C0603
R38: 10k; 0603
R39: 390k; 0603
R40, R41: 4.7k; 0603
U$18: ER-OLED0.96

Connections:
GND: C1.1, C3.1, C37.1, R39.2, U$18.P$8 (8.VSS), U$18.P$10 (10.BS0), U$18.P$12 (12.BS2), U$18.P$13 (13.CS#), U$18.P$15 (15.D/C#), U$18.P$16 (16.R/W#), U$18.P$17 (17.E/RD#), U$18.P$21 (21.D3), U$18.P$22 (22.D4), U$18.P$23 (23.D5), U$18.P$24 (24.D6), U$18.P$25 (25.D7), U$18.P$29 (29.VLSS); also elsewhere on the board
I2C3_SCL: R41.2, U$18.P$18 (18.D0); also elsewhere on the board
I2C3_SDA: R40.1, U$18.P$19 (19.D1), U$18.P$20 (20.D2); also elsewhere on the board
MCU_3V3: R40.2, R41.1; also elsewhere on the board
unnamed: C1.2, R38.2, U$18.P$14 (14.RES#)
unnamed: C2.1, U$18.P$3 (3.C2N)
unnamed: C36.1, U$18.P$5 (5.C1N)
unnamed: C2.2, U$18.P$2 (2.C2P)
unnamed: C36.2, U$18.P$4 (4.C1P)
unnamed: R39.1, U$18.P$26 (26.IREF)
unnamed: C3.2, U$18.P$27 (27.VCOMH)
unnamed: C37.2, U$18.P$28 (28.VCC)
VCC: R38.1, U$18.P$6 (6.VBAT), U$18.P$9 (9.VDD), U$18.P$11 (11.BS1); also elsewhere on the board

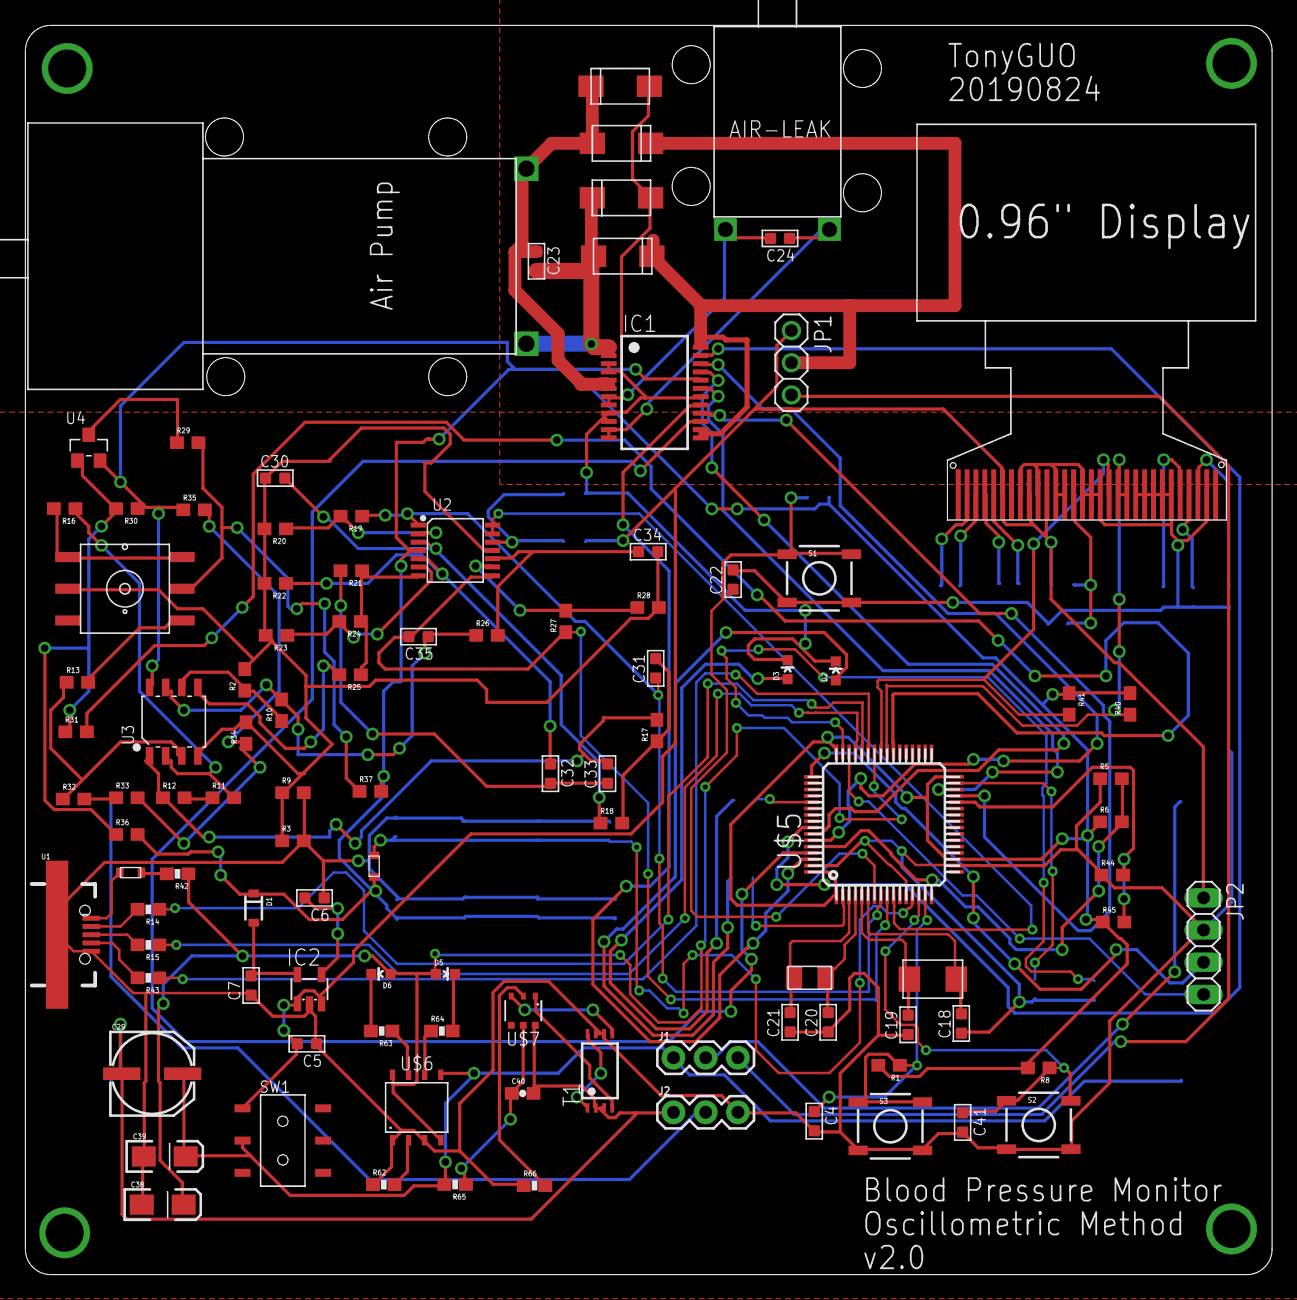
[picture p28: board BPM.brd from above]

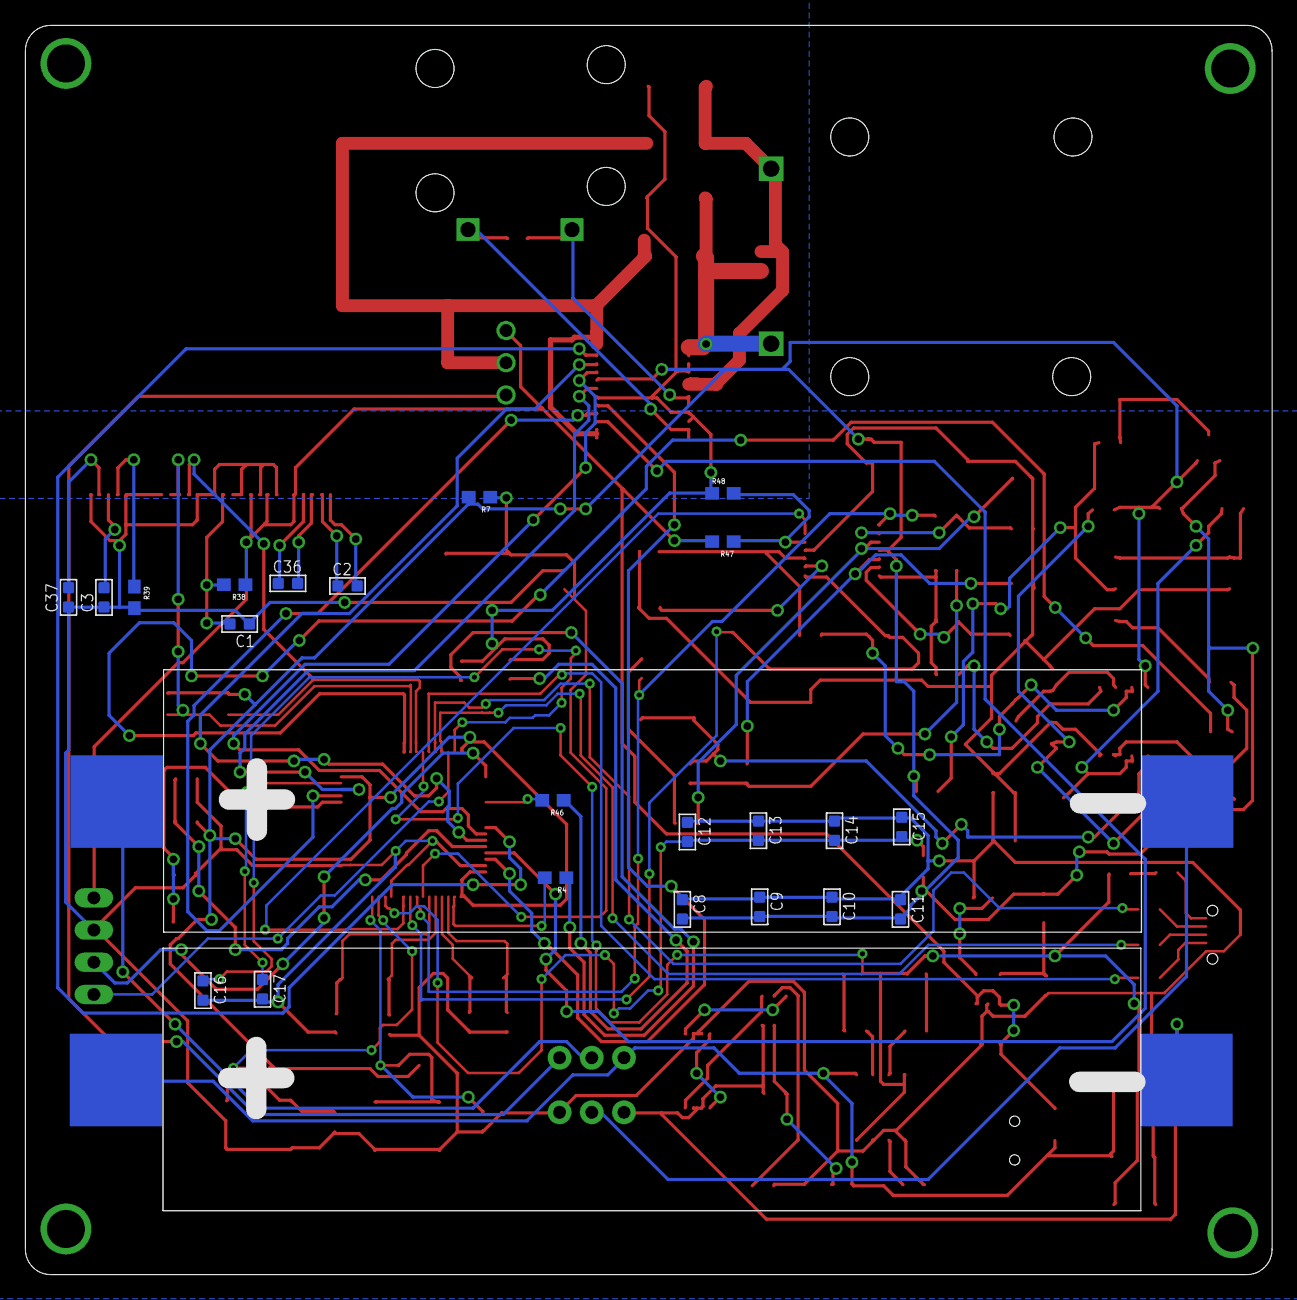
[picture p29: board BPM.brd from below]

Board: 2 copper layers, 98.3 x 98.5 mm, 127 parts (24 on the bottom side), 98 nets.

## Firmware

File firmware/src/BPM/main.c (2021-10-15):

#include <stdio.h>
#include <stdarg.h>
#include <stdbool.h>

#include <stm32f4xx.h>
#include <stm32f4xx_gpio.h>
#include <stm32f4xx_usart.h>
#include <stm32f4xx_exti.h>
#include <stm32f4xx_i2c.h>
#include <stm32f4xx_adc.h>
#include <stm32f4xx_rcc.h>
#include <stm32f4xx_dma.h>
#include <stm32f4xx_rtc.h>
#include <stm32f4xx_tim.h>
#include <stm32f4xx_flash.h>

#include "define.h"

#include "I2C.h"
#include "SSD1306.h"
#include "VCP.h"

#include "FIR.h"
#include "adaptive_algorithm.h"

#include "adc.h"

#include "tiny_printf.h"

#include "pid.h"

#define __FPU_PRESENT
#define __FPU_USED

enum{
   DATA_COLLECTION_MODE = 0,
   CALIBRATION_MODE,
   MERCURY_METER_MODE,
   BPM_MODE,
   AF_MODE
};

const uint32_t SECOND = 1000000;

const uint16_t PWM_Freq = 1000;

volatile uint32_t TimingDelay;

volatile uint32_t micros = 20000000;

const uint32_t FLASH_ADDRESS_AS = 0x080E0020;
const uint32_t FLASH_ADDRESS_AD = 0x080E0024;
float as_am_value = 0.65f;
float ad_am_value = 0.7f;
uint32_t set_as, set_ad;
bool as_ad_is_set = false;

float a[3] = {-0.0000012119f,0.1262915457f,-1.0620516546f};

uint32_t PRESSURE_MIN = 50;
uint32_t PRESSURE_MAX = 160;
const uint32_t STOP_PRESSURE = 180;

uint32_t last_update;
uint32_t last_screen_update;

volatile uint32_t mode = DATA_COLLECTION_MODE;
volatile bool is_pressurize = false;
volatile bool is_leak = false;

const uint32_t CALIBRATION_PRESSURIZE_TIME = 300000;	//300ms
const uint32_t CALIBRATION_LEAK_TIME = 120000;	//120ms
const uint32_t CALIBRATION_HIGH_SLOP_THRESHOLD = 1500;

bool measure_flag = false;
bool calibration_flag = false;

float last_pressure = 0;
float diff_pressure = 0;
float pwm = 0,setpoint = 3;
float Kp = 2.8, Ki = 0.3, Kd = 0.2;
const uint32_t FLASH_ADDRESS_P = 0x080E0010;
const uint32_t FLASH_ADDRESS_I = 0x080E0014;
const uint32_t FLASH_ADDRESS_D = 0x080E0018;
const uint32_t FLASH_ADDRESS_SP = 0x080E001C;
uint32_t set_kp,set_ki,set_kd,set_sp;
bool pid_is_set = false;

const uint32_t PID_PWM_MIN = 1;
const uint32_t PID_PWM_MAX = 100;
const uint32_t TIMER_PWM_MIN = 100000;
const uint32_t TIMER_PWM_MAX = 1000000;
const uint32_t TIMER_PWM_33 = 330000;
const uint32_t TIMER_PWM_40 = 400000;

float baseline = 0;
float dc = 0;
uint32_t init_baseline_count = 0;  

float pressure = 0; // mmHg

float MAP;
float SBP;
float DBP;

static const uint32_t MEASURMENT_TIME = 35;
float dc_array[70];	//size = MEASURMENT_TIME * 2
float ac_array[70];	//size = MEASURMENT_TIME * 2
uint32_t index_array[70];	//size = MEASURMENT_TIME * 2
uint32_t pulse_index;

volatile uint32_t last_AF = 0;
volatile uint32_t AF_counter = 0;
const uint32_t AF_PERIOD = 8; //SENCOND
uint32_t IPP = 0;
uint32_t IHB = 0;
const float IPP_Ratio = 0.2f;
const float IHB_Ratio = 0.2f;

const unsigned int taps = 19;
/*100hz 0.7Hz~8.9Hz*/
float coeff1[19] = {-0.043047,-0.048389,-0.042549,-0.023677,0.0073069,0.046611,0.088179,0.12489,0.15008,0.15905,0.15008,0.12489,0.088179,0.046611,0.0073069,-0.023677,-0.042549,-0.048389,-0.043047};
/* 100Hz 0.5Hz low pass*/
float coeff2[19] = {0.050186,0.050989,0.051705,0.052331,0.052864,0.053303,0.053646,0.053892,0.05404,0.054089,0.05404,0.053892,0.053646,0.053303,0.052864,0.052331,0.051705,0.050989,0.050186};
float buffer1[19];
unsigned offset1;
float buffer2[19];
unsigned offset2;

FIRInfo info1;
FIRInfo info2;

uint32_t time_to_index = 0;

uint32_t detect_time = 0;

bool mercury_meter_flag = false;

void Delay(__IO uint32_t nTime)
{
   TimingDelay = nTime;
   while(TimingDelay){
   }
}

void SysTick_Handler(void)
{
   if(TimingDelay){
      --TimingDelay;
   }
   ++micros;
}

void Init_LED()
{
   //Enable the GPIOD Clock
   RCC_AHB1PeriphClockCmd(RCC_AHB1Periph_GPIOC,ENABLE);


   // GPIOD Configuration
   GPIO_InitTypeDef GPIO_InitStruct;
   GPIO_InitStruct.GPIO_Pin = GPIO_Pin_12 | GPIO_Pin_13;
   GPIO_InitStruct.GPIO_Mode = GPIO_Mode_OUT;
   GPIO_InitStruct.GPIO_Speed = GPIO_Speed_50MHz;
   GPIO_InitStruct.GPIO_OType = GPIO_OType_PP;
   GPIO_InitStruct.GPIO_PuPd = GPIO_PuPd_UP;

   //GPIO_SetBits(GPIOC, GPIO_Pin_12);
   //GPIO_SetBits(GPIOC, GPIO_Pin_13);
   GPIO_Init(GPIOC, &GPIO_InitStruct);   
}

void EXTILine0_Config(void)
{
   EXTI_InitTypeDef   EXTI_InitStructure;
   GPIO_InitTypeDef   GPIO_InitStructure;
   NVIC_InitTypeDef   NVIC_InitStructure;

   /* Enable GPIOB clock */
   RCC_AHB1PeriphClockCmd(RCC_AHB1Periph_GPIOA, ENABLE);
   /* Enable SYSCFG clock */
   RCC_APB2PeriphClockCmd(RCC_APB2Periph_SYSCFG, ENABLE);

   /* Configure PB0 pin as input floating */
   GPIO_InitStructure.GPIO_Mode = GPIO_Mode_IN;
   GPIO_InitStructure.GPIO_PuPd = GPIO_PuPd_NOPULL;
   GPIO_InitStructure.GPIO_Pin = GPIO_Pin_0;
   GPIO_Init(GPIOA, &GPIO_InitStructure);

   /* Connect EXTI Line0 to PB0 pin */
   SYSCFG_EXTILineConfig(EXTI_PortSourceGPIOA, EXTI_PinSource0);

   /* Configure EXTI Line0 */
   EXTI_InitStructure.EXTI_Line = EXTI_Line0;
   EXTI_InitStructure.EXTI_Mode = EXTI_Mode_Interrupt;
   EXTI_InitStructure.EXTI_Trigger = EXTI_Trigger_Rising_Falling;  
   EXTI_InitStructure.EXTI_LineCmd = ENABLE;
   EXTI_Init(&EXTI_InitStructure);

   /* Enable and set EXTI Line0 Interrupt to the lowest priority */
   NVIC_InitStructure.NVIC_IRQChannel = EXTI0_IRQn;
   NVIC_InitStructure.NVIC_IRQChannelPreemptionPriority = 1;
   NVIC_InitStructure.NVIC_IRQChannelSubPriority = 0;
   NVIC_InitStructure.NVIC_IRQChannelCmd = ENABLE;
   NVIC_Init(&NVIC_InitStructure);
}

void EXTILine1_Config(void)
{
   EXTI_InitTypeDef   EXTI_InitStructure;
   GPIO_InitTypeDef   GPIO_InitStructure;
   NVIC_InitTypeDef   NVIC_InitStructure;

   /* Enable GPIOB clock */
   RCC_AHB1PeriphClockCmd(RCC_AHB1Periph_GPIOA, ENABLE);
   /* Enable SYSCFG clock */
   RCC_APB2PeriphClockCmd(RCC_APB2Periph_SYSCFG, ENABLE);

   /* Configure PB0 pin as input floating */
   GPIO_InitStructure.GPIO_Mode = GPIO_Mode_IN;
   GPIO_InitStructure.GPIO_PuPd = GPIO_PuPd_NOPULL;
   GPIO_InitStructure.GPIO_Pin = GPIO_Pin_1;
   GPIO_Init(GPIOA, &GPIO_InitStructure);

   /* Connect EXTI Line0 to PB0 pin */
   SYSCFG_EXTILineConfig(EXTI_PortSourceGPIOA, EXTI_PinSource1);

   /* Configure EXTI Line0 */
   EXTI_InitStructure.EXTI_Line = EXTI_Line1;
   EXTI_InitStructure.EXTI_Mode = EXTI_Mode_Interrupt;
   EXTI_InitStructure.EXTI_Trigger = EXTI_Trigger_Rising_Falling;  
   EXTI_InitStructure.EXTI_LineCmd = ENABLE;
   EXTI_Init(&EXTI_InitStructure);

   /* Enable and set EXTI Line0 Interrupt to the lowest priority */
   NVIC_InitStructure.NVIC_IRQChannel = EXTI1_IRQn;
   NVIC_InitStructure.NVIC_IRQChannelPreemptionPriority = 1;
   NVIC_InitStructure.NVIC_IRQChannelSubPriority = 1;
   NVIC_InitStructure.NVIC_IRQChannelCmd = ENABLE;
   NVIC_Init(&NVIC_InitStructure);
}

void Init_PWM()
{
   //Enable the GPIOD Clock
   RCC_AHB1PeriphClockCmd(RCC_AHB1Periph_GPIOC,ENABLE);


   // GPIOD Configuration
   GPIO_InitTypeDef GPIO_InitStruct;
   GPIO_InitStruct.GPIO_Pin = GPIO_Pin_8;
   GPIO_InitStruct.GPIO_Mode = GPIO_Mode_OUT;
   GPIO_InitStruct.GPIO_Speed = GPIO_Speed_50MHz;
   GPIO_InitStruct.GPIO_OType = GPIO_OType_PP;
   GPIO_InitStruct.GPIO_PuPd = GPIO_PuPd_UP;

   GPIO_Init(GPIOC, &GPIO_InitStruct);   

   //GPIO_SetBits(GPIOC, GPIO_Pin_8);
   GPIO_ResetBits(GPIOC, GPIO_Pin_8);
}

void Init_TB6612FNG()
{
   //Enable the GPIOD Clock
   RCC_AHB1PeriphClockCmd(RCC_AHB1Periph_GPIOB,ENABLE);


   // GPIOD Configuration
   GPIO_InitTypeDef GPIO_InitStruct;
   GPIO_InitStruct.GPIO_Pin = GPIO_Pin_6 | GPIO_Pin_7 | GPIO_Pin_8 | GPIO_Pin_9 | GPIO_Pin_10 | GPIO_Pin_11;
   GPIO_InitStruct.GPIO_Mode = GPIO_Mode_OUT;
   GPIO_InitStruct.GPIO_Speed = GPIO_Speed_50MHz;
   GPIO_InitStruct.GPIO_OType = GPIO_OType_PP;
   GPIO_InitStruct.GPIO_PuPd = GPIO_PuPd_UP;

   GPIO_Init(GPIOB, &GPIO_InitStruct); 

   GPIO_SetBits(GPIOB, GPIO_Pin_6);
   GPIO_ResetBits(GPIOB, GPIO_Pin_7);
   //GPIO_SetBits(GPIOB, GPIO_Pin_8);
   GPIO_ResetBits(GPIOB, GPIO_Pin_8);
   GPIO_ResetBits(GPIOB, GPIO_Pin_9);
   GPIO_SetBits(GPIOB, GPIO_Pin_10);
   GPIO_SetBits(GPIOB, GPIO_Pin_11);
}

void MOTOR_PWM_Config(uint16_t PWM_Freq)
{
   TIM_TimeBaseInitTypeDef  TIM_TimeBaseStructure;
   TIM_OCInitTypeDef  TIM_OCInitStructure;	
   GPIO_InitTypeDef GPIO_InitStructure;

   uint16_t PrescalerValue = 0;

   /* TIM3 clock enable */
   RCC_APB1PeriphClockCmd(RCC_APB1Periph_TIM3, ENABLE);

   /* GPIOC clock enable */
   RCC_AHB1PeriphClockCmd(RCC_AHB1Periph_GPIOB, ENABLE);


   /* GPIOC Configuration: TIM3 CH3 (PC8) */
   GPIO_InitStructure.GPIO_Pin = GPIO_Pin_5;
   GPIO_InitStructure.GPIO_Mode = GPIO_Mode_AF;
   GPIO_InitStructure.GPIO_Speed = GPIO_Speed_100MHz;
   GPIO_InitStructure.GPIO_OType = GPIO_OType_PP;
   GPIO_InitStructure.GPIO_PuPd = GPIO_PuPd_UP ;
   GPIO_Init(GPIOB, &GPIO_InitStructure); 

   /* Connect TIM3 pins to AF2 */
   GPIO_PinAFConfig(GPIOB, GPIO_PinSource5, GPIO_AF_TIM3);

   /* Compute the prescaler value */
   PrescalerValue = (uint16_t) ((SystemCoreClock /2) / 1000000) - 1; // (168000000/2)/1000000 = 84

   /* Time base configuration */
   TIM_TimeBaseStructure.TIM_Period = TIMER_PWM_MAX/PWM_Freq;
   TIM_TimeBaseStructure.TIM_Prescaler = PrescalerValue;
   TIM_TimeBaseStructure.TIM_ClockDivision = TIM_CKD_DIV1;
   TIM_TimeBaseStructure.TIM_CounterMode = TIM_CounterMode_Up;
   TIM_TimeBaseInit(TIM3, &TIM_TimeBaseStructure);

   /* PWM1 Mode configuration: Channel3 */
   TIM_OCInitStructure.TIM_OutputState = TIM_OutputState_Enable;
   //TIM_OCInitStructure.TIM_Pulse = 500000/PWM_Fren; //50% duty cycle
   TIM_OCInitStructure.TIM_Pulse = 0;
   TIM_OCInitStructure.TIM_OCMode = TIM_OCMode_Inactive;

   TIM_OC3Init(TIM3, &TIM_OCInitStructure);
   TIM_OC3PreloadConfig(TIM3, TIM_OCPreload_Enable);
   TIM_ARRPreloadConfig(TIM3, ENABLE);

   /* TIM3 enable counter */
   //TIM_Cmd(TIM3, ENABLE);	


}

void MOTOR_PWM_out(uint16_t PWM_Freq)
{

   if(PWM_Freq){
      //TIM_Cmd(TIM3, DISABLE);
      TIM3->ARR = (TIMER_PWM_MAX/PWM_Freq)-1; //TIM_Period
      TIM3->CCR2 = 0; //TIM_Pulse
      TIM_SelectOCxM(TIM3, TIM_Channel_2, TIM_OCMode_PWM1);
      TIM_CCxCmd(TIM3, TIM_Channel_2, TIM_CCx_Enable);
      TIM3->EGR = TIM_EventSource_Update;
      TIM_Cmd(TIM3, ENABLE);	 
   }
   else{
      TIM_Cmd(TIM3, DISABLE);
      TIM_SelectOCxM(TIM3, TIM_Channel_2, TIM_ForcedAction_InActive);
      TIM_CCxCmd(TIM3, TIM_Channel_2, TIM_CCx_Enable);		 
   }

}

void WriteParameters2FLASH()
{

   FLASH_Unlock();
   FLASH_ClearFlag( FLASH_FLAG_EOP |  FLASH_FLAG_WRPERR | FLASH_FLAG_PGAERR | FLASH_FLAG_PGPERR | FLASH_FLAG_PGSERR);
   FLASH_EraseSector(FLASH_Sector_11,VoltageRange_3);
   FLASH_ProgramWord(FLASH_ADDRESS_P,set_kp);
   FLASH_ProgramWord(FLASH_ADDRESS_I,set_ki);
   FLASH_ProgramWord(FLASH_ADDRESS_D,set_kd);
   FLASH_ProgramWord(FLASH_ADDRESS_SP,set_sp);

   FLASH_ProgramWord(FLASH_ADDRESS_AS,set_as);
   FLASH_ProgramWord(FLASH_ADDRESS_AD,set_ad);
   
   FLASH_Lock();
}

void SetPIDParameter()
{
   uint8_t c;
   char pid_str[18];
   int i = 0;
   while(USB_VCP_Getc(&c) == USB_VCP_DATA_OK){
      if(c == 'l' || c == 'L'){
	 char p_str[5]="", i_str[5]="", d_str[5]="", sp_str[5]="";
	 p_str[0] = pid_str[0];p_str[1] = pid_str[1];p_str[2] = pid_str[2];p_str[3] = pid_str[3];
	 i_str[0] = pid_str[4];i_str[1] = pid_str[5];i_str[2] = pid_str[6];i_str[3] = pid_str[7];
	 d_str[0] = pid_str[8];d_str[1] = pid_str[9];d_str[2] = pid_str[10];d_str[3] = pid_str[11];
	 sp_str[0] = pid_str[12];sp_str[1] = pid_str[13];sp_str[2] = pid_str[14];sp_str[3] = pid_str[15];

	 set_kp = atoi(p_str);
	 set_ki = atoi(i_str);
	 set_kd = atoi(d_str);
	 set_sp = atoi(sp_str);
	 set_as = *(uint32_t*)FLASH_ADDRESS_AS;
	 set_ad = *(uint32_t*)FLASH_ADDRESS_AD;

	 pid_is_set = true;

	 WriteParameters2FLASH();    

	 break;
      }
      pid_str[i++] = c;
   }

}
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

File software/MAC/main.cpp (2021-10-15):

#include <wx/wx.h>
#include <wx/filename.h>
#include <wx/tokenzr.h>
#include <wx/valnum.h>
#include <wx/thread.h>
#include <wx/stdpaths.h>

#include <fstream>
#include <cmath>
#include <cstdlib>
#include <ctime> 
#include <iostream>
#include <chrono> 
#include <iomanip>
#include <sstream>
#include <string>

#include "mathplot.h"
#include "connectargsdlg.h"
#include "pidargsdlg.h"
#include "bpalgodlg.h"
#include "serialport.h"

#include "define.h"
#include "adaptive_algorithm.h"
#include "FIR.h"
#include "polynomial_regression.h"

const unsigned int taps = 19;
/*100hz 0.7Hz~8.9Hz*/
float coeff1[taps] = {-0.043047,-0.048389,-0.042549,-0.023677,0.0073069,0.046611,0.088179,0.12489,0.15008,0.15905,0.15008,0.12489,0.088179,0.046611,0.0073069,-0.023677,-0.042549,-0.048389,-0.043047};
/* 100Hz 0.5Hz low pass*/
float coeff2[taps] = {0.050186,0.050989,0.051705,0.052331,0.052864,0.053303,0.053646,0.053892,0.05404,0.054089,0.05404,0.053892,0.053646,0.053303,0.052864,0.052331,0.051705,0.050989,0.050186};

float buffer1[taps];
unsigned offset1;
float buffer2[taps];
unsigned offset2;

enum{
   ID_EXIT = 200,
   ID_OPEN,
   ID_RECORD,
   ID_VCP,
   ID_CLEAR_ALL_PLOT,
   ID_CONNECT_DEVICE,
   ID_PID_TUNING,
   ID_AS_AD_TUNING,
   ID_MEASUREMENT,
   ID_PRESSURIZE,
   ID_MERCURY_METER,
   ID_LEAK,
   ID_MODE
};

enum{
   EVT_SERIAL_PORT_READ = 625,
   EVT_REFRESH_PLOT
};

enum{
   ID_THREAD = 9999
};

class Thread;

class App:public wxApp
{
   public:
      bool OnInit();
};

class Frame:public wxFrame
{
   public:
      Frame(const wxString&);
      ~Frame();

      void CreateUI();

      void OnProcess(wxCommandEvent&);

      void OnClearAllPlot(wxCommandEvent&);
      void OnOpen(wxCommandEvent&);
      void OnKeyDown(wxKeyEvent& event);
      void OnConnectDevice(wxCommandEvent&);
      void OnPIDTuning(wxCommandEvent&);
      void OnAsAdTuning(wxCommandEvent&);
      void OnMeasurment(wxCommandEvent&);
      void OnMercuryMeter(wxCommandEvent&);
      void OnPressurize(wxCommandEvent&);
      void OnLeak(wxCommandEvent&);
      void OnMode(wxCommandEvent&);
      void OnExit(wxCommandEvent&);

      void ReadCurve();
      void BPCalculator();

      void ClearAllData();

      void OnFit(wxCommandEvent&);

      void OnThreadEvent(wxThreadEvent &event);

   private:

      void split(const std::string& s, std::vector<std::string>& sv, const char delim = ' '){
	 sv.clear();
	 std::istringstream iss(s);
	 std::string temp;

	 while (std::getline(iss, temp, delim)){
	    sv.emplace_back(std::move(temp));
	 }
      }      

      wxMenu *vcp;
      wxThread *thread;

      SerialPort serial;     
      bool is_open;

      bool run_flag;

      mpWindow *dc_plot;
      mpWindow *ac_plot;  

      mpFXYVector* dc_layer;
      std::vector<double> dc_layer_x, dc_layer_y;
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

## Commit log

2019-10-17 t-type and direct connector
2019-11-03 Eagle PCB - AF-BPM v2
    [BPM.brd, BPM.sch]
2019-11-03 GUI Software
    [curve.csv]
2019-11-03 STM32F405 Firmware
2019-11-10 calibration example

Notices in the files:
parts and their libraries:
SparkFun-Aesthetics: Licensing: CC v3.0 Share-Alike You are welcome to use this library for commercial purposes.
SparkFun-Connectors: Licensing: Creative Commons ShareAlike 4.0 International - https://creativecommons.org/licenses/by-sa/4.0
